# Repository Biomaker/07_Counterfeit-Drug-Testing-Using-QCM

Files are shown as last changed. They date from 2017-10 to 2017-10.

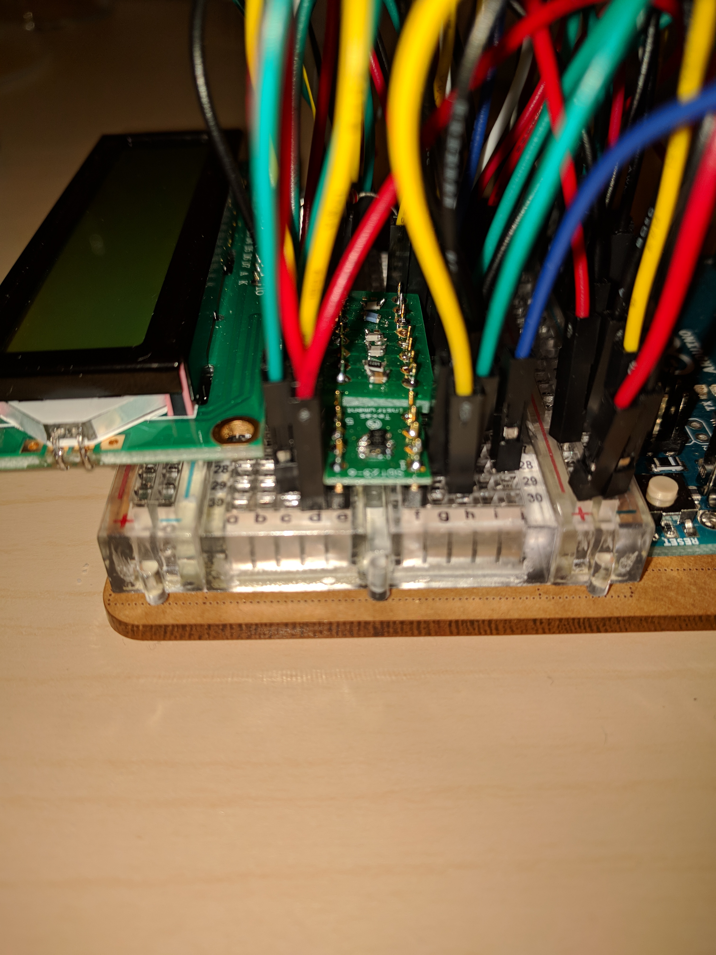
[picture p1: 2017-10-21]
Images/Surface_mount_components.jpg

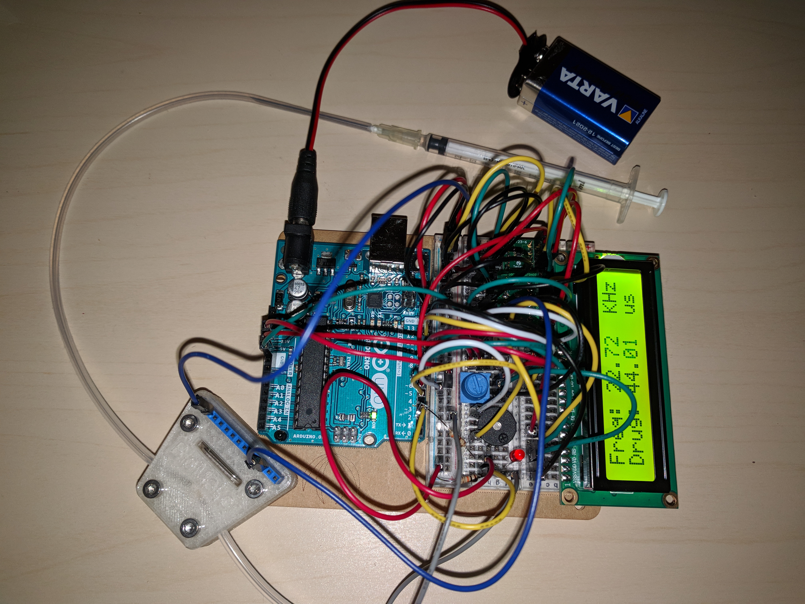
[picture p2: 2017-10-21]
Images/Complete_Setup.jpg

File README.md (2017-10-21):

## Synopsis

Malaria kills approximately a million people each year, and although efforts to produce and distribute effective drugs has increased, there is a growing problem with forged medications. Counterfeit antimalarial drugs cause an estimated 120,000 deaths in Africa per year , and detection methods are too expensive and/or too technically complex. Our objective is the development of a low cost counterfeit drug detection system that can be easily used in low-resource settings. The system builds on open-source quartz crystal microbalance technology to detect the presence of the active drug and its concentration. Easily contained in a handheld device that will give real-time feedback to the user, our method ensures the efficacy of global health measures by contributing to effective malaria elimination in at-risk communities.

## Software

The frequency output of the oscilator was connected to Arduino pin 5 as this is this pin must be used on the Arduino Uno when using the 16bit Timer/Counter1 of the ATmega chip as our code does.
The LCD was connected to pins 8,9,10,6,12,13 corresponding to RS,E,D4,D5,D6,D7 on our LCD display. Pin 6 was used instead of pin 11 as we anticipated using a buzzer output with the inbuilt "tone" function which can cause instabilities on pins 3 and 11. 

## Hardware

The included electrical schematics were used to set up the device. However the thermoresitor was excluded from our final implementation (couldn't get it to read in a reasonable valure).

The included CAD models were printed on an Ulitimaker 3. The inlet ports were connected to 2mm OD Silicone tubing whihc caused a press fit.

Rubber nitrile o-rings were used to support the QCM and form a seal.

M3 nuts and bolts were used to clamp the assembly together.

## Installation, Maintenance and Testing Guide

The frequency output of the oscilator was directed to pin 5 and written to the connected LCD.

Ideally this value would be compared to a stored value for the expected frequency response of the target analyte.

Pins 8-13 were used for readout to the LCD display

## License

A short snippet describing the license (MIT, Apache, etc.) you have chosen to use

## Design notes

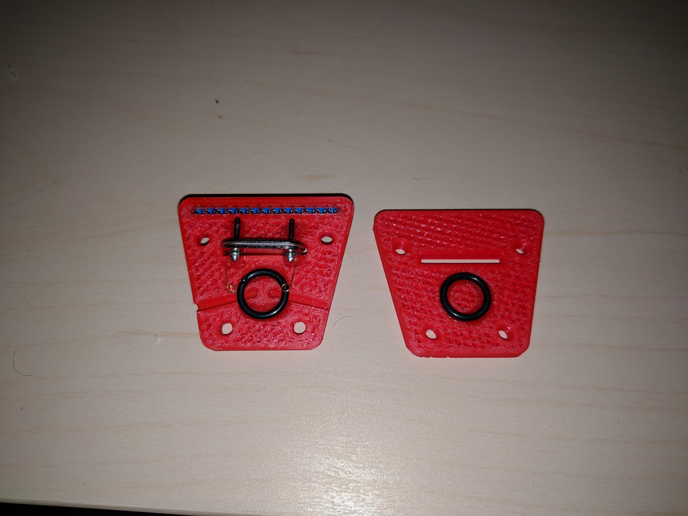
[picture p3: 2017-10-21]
Images/Internal_Channel.jpg

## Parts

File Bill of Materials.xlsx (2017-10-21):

Part | Minimum Order | Cost Per Order | Cost Per Unit | Required Units | Supplier | Part Number
3D printed | 750 | 30 | 0.8 | 1 | Ulitimaker
Socket Strip 2.54mm 14 Way 1 Row Straight PCB Socket Through Hole | 20 | 30.16 | 1.508 | 1 | RS | 252-406
Crystal Oscillator Driver | 10 | 7.81 | 0.781 | 1 | Texas Instruments | SN74LVC1GX04DBVT
Thick Film Resistors - SMD 1/8watt 1Kohms 1% 100ppm | 10 | 1.4 | 0.14 | 1 | RS | 679-0982
Thick Film Resistors - SMD 1/8watt 2.26Mohms 1% | 10 | 0.017 | 0.0017 | 1 | Vishay | CRCW08052M26FKEA
Multilayer Ceramic Capacitors MLCC - SMD/SMT 50volts 0.1uF X7R 10% | 10 | 0.45 | 0.045 | 1 | Kemet | C0805C104K5RACTU
Multilayer Ceramic Capacitors MLCC - SMD/SMT 50volts 100pF C0G 5% | 20 | 0.65 | 0.065 | 2 | Kemet | C0805C101J5GACTU
RESISTOR, 10KOHM, 0.125W | 10 | 0.65 | 0.065 | 1 | Onecall | 2352781
Thermistors - NTC 10Kohms 1% | 10 | 4.7 | 0.47 | 1 | OneCall | 2112901
Contact Clip Circuit Board Hardware - PCB | 20 | 2.18 | 0.218 | 2 | Harwin | S9101-46R
Quartz Crystal 10 Mhz Au electrode 13.9 x 6 mm | 10 | 114 | 11.4 | 1 | Open QCM | AT10-14-6-UP-10
Quartz Crystal holder | 10 | 17.5 | 1.75 | 1 | Open QCM | HC-48/U-EV
Nitrile Rubber O-Ring, 8.1mm Bore , 11.3mm O.D , -30 → +120°C | 50 | 2.92 | 0.1168 | 2 | RS | 0081-16 NBR
Syringe | 100 | 8.56 | 0.0856 | 1
Tubing | 50 | 36 | 0.72 | 20mm
M3 bolt + nut |  | 0.2516 | 0.7548 | 4
Total Cost per setup |  |  | 18.9209

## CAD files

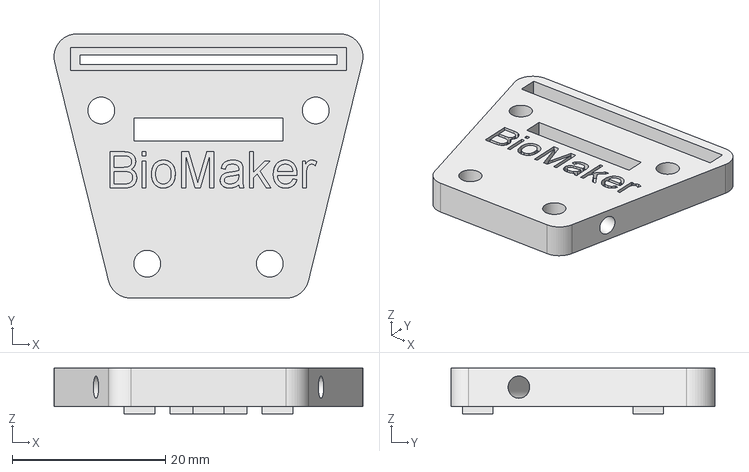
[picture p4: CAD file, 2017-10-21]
CAD Files/Top_v2.FCStd
40.3 x 34.5 x 6.00 mm

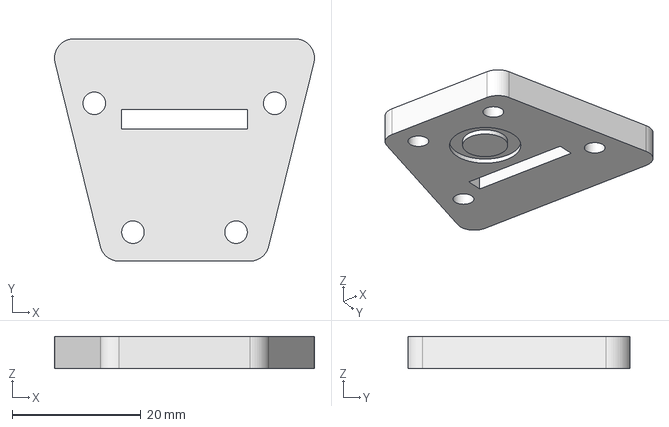
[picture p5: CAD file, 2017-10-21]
CAD Files/Base_v2.FCStd
40.3 x 34.5 x 5.00 mm

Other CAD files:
CAD Files/base_v2.stl
CAD Files/top_v2.stl

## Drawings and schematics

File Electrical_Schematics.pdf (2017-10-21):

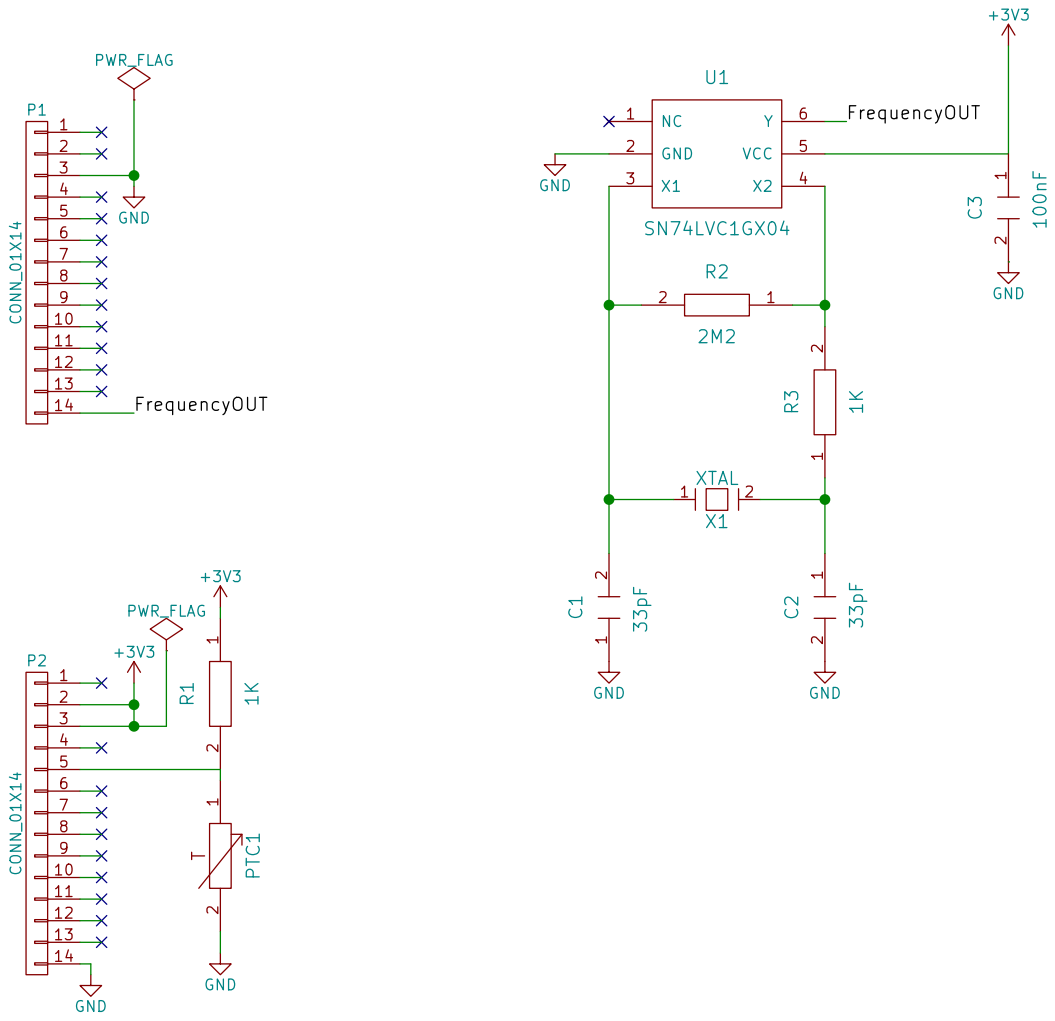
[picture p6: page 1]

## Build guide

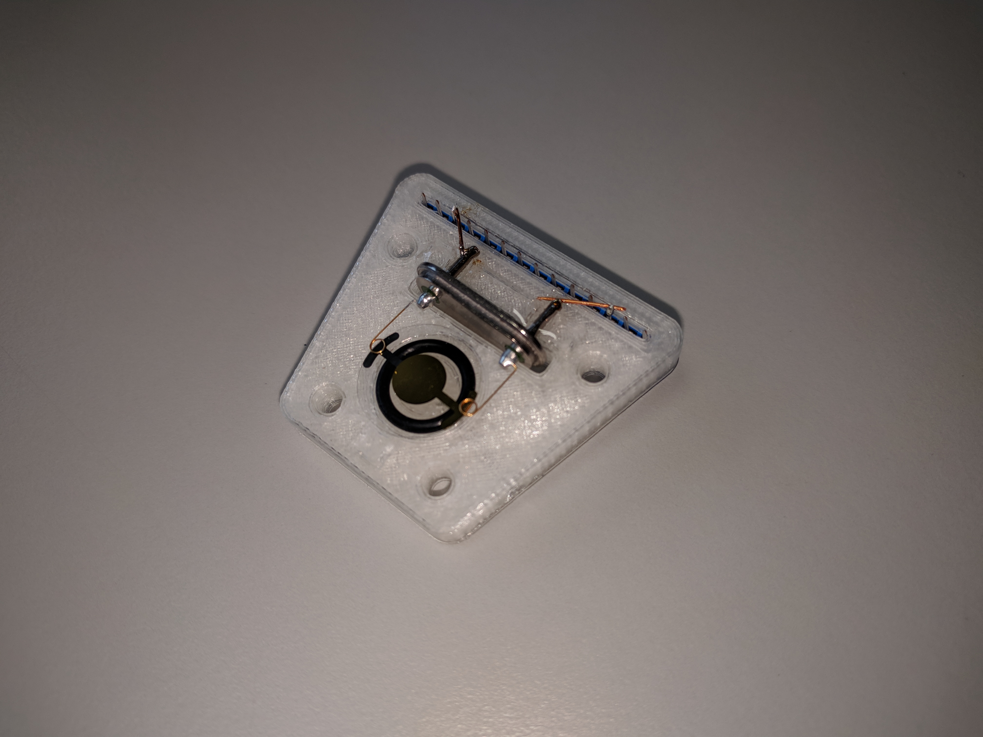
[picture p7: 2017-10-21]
Images/Internal_Crystal_Wiring.jpg

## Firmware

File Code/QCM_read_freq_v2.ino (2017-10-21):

/*  QCM Sensor With LCD - by Jason Brenker -Oct 2017 - adapted from Frequency Counter With LCD Display arduinoaleman - May 2015 

    Pin D5 of Arduino must be used for frequency input. The LCD uses pins 8 thru 13.
  
    Counter1 : 16 bits / used to count the frequency impules
    Counter2 : 8 bits / used to genarate a 1000ms or 100ms gate time for measurement
    
    Uses "bitClear(TIMSK0,TOIEO)" instead of "TIMSK0 &=~(1<<TOIE0)"
    Uses "bitSet(TIMSK0,TOIEO)"   instead of "TIMSK0 |=~(1<<TOIE0)"
   
 */

//Libraries for reading frequency and writing to display
#include <avr/interrupt.h>
#include <LiquidCrystal.h>

//Currently not used included for when a buzzer is included in design
#include "pitches.h"

//Sets pins for display, note pin 6 is used because when tone is implemented pin 11 could experience issues
LiquidCrystal lcd(8,9,10,6,12,13);

volatile unsigned long frequency=0;            
volatile boolean       measurement_ready;
volatile unsigned char overflow_counter;     // number of overflows within gate_time
volatile unsigned int  time_so_far;              // number of ISR calls
volatile unsigned int  gate_time;  

//This is currently not used, included to look for button press to activate measurment mode
// constants won't change. They're used here to set pin numbers:
const int buttonPin = 2;     // the number of the pushbutton pin
const int ledPin =  3;      // the number of the LED pin
// variables will change:
int buttonState = 0;         // variable for reading the pushbutton status

void measurement(int ms) {

    bitClear(TIMSK0,TOIE0);     // disable counter0 in order to disable millis() and delay()
                                   // this will prevent extra interrupts that disturb the measurement
    delayMicroseconds(66);      // wait for other interrupts to finish
    gate_time=ms;                  // usually 1000 (ms)

    // setup of counter 1 which will be used for counting the signal impulses
    TCCR1A=0;                  // reset timer/counter1 control register A
    TCCR1B=0;                  // reset timer/counter1 control register B
    TCCR2A=0;                  // reset timer/counter1 control register A
    TCCR2B=0;                  // reset timer/counter2 control register A
    
    // setup of counter2 which will be used to create an interrupt every millisecond (used for gate time)

    TCCR2B |= B00000101;        // set prescale factor of counter2 to 128 (16MHz/128 = 125000Hz)
                                   // by setting CS22=1, CS21=0, CS20=1

    bitSet(TCCR2A,WGM21) ;      // set counter2 to CTC mode
                                   // WGM22=0, WGM21=1, WGM20=0                   
    OCR2A = 124;                   // CTC divider will divide 125Kz by 125 
   
    measurement_ready=0;        // reset
    time_so_far=0;              // reset
    bitSet(GTCCR,PSRASY);       // reset the prescaler 
    TCNT1=0;                    // set frequency counter1 to 0
    TCNT2=0;                    // set gate time counter2 to 0
      
    bitSet(TIMSK2,OCIE2A);      // enable counter2 interrupts
    TCCR1B |= B00000111;        // set CS12, CS11 and CS10 to "1" which starts counting 
                                // on T1 pin (Arduino pin D5)
 }

ISR(TIMER2_COMPA_vect) {
   if (time_so_far >= gate_time) {  // end of gate time, measurement is ready
    TCCR1B &= B11111000;            // stop counter1 by setting CS12, CS11 and CS10 to "0"
    bitClear(TIMSK2,OCIE2A);        // disable counter2 interrupts
    bitSet(TIMSK0,TOIE0);           // enable Timer0 again // millis and delay
    measurement_ready=true;         // set global flag for end count period
// calculate now frequeny value 
    frequency=0x10000 * overflow_counter;  // mult #overflows by 65636 (0x10000)
    frequency += TCNT1;                    // add counter1 contents for final value
    overflow_counter=0;                    // reset overflow counter
  }
   else {
    time_so_far++;                         // count number of interrupt events
    if bitRead(TIFR1,TOV1)  {              // if Timer/Counter 1 overflow flag = "1" then ...
       overflow_counter++;                 // increase number of counter1 overflows
       bitSet(TIFR1,TOV1);                 // reset counter1 overflow flag
    }
  };
}

void setup() {
  // initialize the LED pin as an output:
  pinMode(ledPin, OUTPUT);
  // initialize the pushbutton pin as an input:
  pinMode(buttonPin, INPUT);
  pinMode(5,INPUT);
  lcd.begin(16, 2);            // defines a LCD with 16 columns and 2 rows
  lcd.clear();
  for (int row=0; row<=1; row++) {
     for (int column=0; column<=15; column++) {   // LDC test
      lcd.setCursor(column,row);
       lcd.print("*");
       delay(70);
      };
  }
  lcd.clear();
}

void loop() {
  float period;    
  float floatfrq;  
  int range;
  long frq;
  measurement(1000);       // 1000ms standard gate time
  while (measurement_ready==false);
  frq=frequency;
  floatfrq=frq;                    // type conversion (required!!)
  period=(1/floatfrq);                // period = 1/Frequenz - 

  if ((frq >= 0)&& (frq < 10)) {
    range=0;
      };                                             // Hertz
  if ((frq >= 10)&& (frq < 100)) {
    range=1;
    };   
  if ((frq >= 100)&& (frq < 1000)&& (buttonState == HIGH)) {
    range=7;
    };
  if ((frq >= 100)&& (frq < 1000)) {
    range=2;
    };
  if ((frq >= 1000)&& (frq < 10000)) {
    range=3; floatfrq=floatfrq/1000;
    };      // KHz
  if ((frq >= 10000)&& (frq < 100000)) {
    range=4; floatfrq=floatfrq/1000;
    };
  if ((frq >= 100000)&& (frq < 1000000)) {
    range=5; floatfrq=floatfrq/1000;
    };
  if (frq >= 1000000) {
    range=6; floatfrq=floatfrq/1000000;
    };          // MHz 
  
  lcd.setCursor(0, 0);                 
  lcd.print("Freq:           ");        
  lcd.setCursor(0, 1);                 
  lcd.print("Drug:          ");
   
  switch(range) {             
    case 0:                                          // 1Hz thru 10Hz
       lcd.setCursor(6, 0);   lcd.print(frq);
       lcd.setCursor(10,0);   lcd.print("Hz ");
       lcd.setCursor(5, 1);  lcd.print("Not Present");  
       digitalWrite(ledPin, LOW);
       break;
    case 1:   // 10Hz thru 100Hz
       period=period*1000;        // convert from seconds to ms       
       lcd.setCursor(6, 0);   lcd.print(frq);
       lcd.setCursor(13,0);   lcd.print("Hz ");    
       lcd.setCursor(5, 1);  lcd.print("Not Present");  
       digitalWrite(ledPin, LOW);
       break;
    case 2:    // 100Hz thru 1KHz
       period=period*1000; 
       lcd.setCursor(6, 0);   lcd.print(frq);
       lcd.setCursor(13,0);   lcd.print("Hz ");    
       lcd.setCursor(5, 1);  lcd.print("Not Present");
       digitalWrite(ledPin, LOW);             
       break;
    case 3:    // 1KHz thru 10KHz
       period=period*1000; 
       lcd.setCursor(6, 0);   lcd.print(floatfrq,3);
       lcd.setCursor(13,0);   lcd.print("KHz");    
       lcd.setCursor(5, 1);  lcd.print("DRUG FOUND!"); 
       digitalWrite(ledPin, HIGH);            
       break;
     case 4:   // 10KHz thru 100KHz
       period=period*1000*1000;                  
       lcd.setCursor(6, 0);   lcd.print(floatfrq,2);
       lcd.setCursor(13,0);   lcd.print("KHz");    
       lcd.setCursor(5, 1);  lcd.print("Not Present"); 
       digitalWrite(ledPin, LOW);       
       break;
      case 5:   // 100KHz thru 1MHz
       period=period*1000*1000;                      // convert from s to µ
       lcd.setCursor(6, 0);   lcd.print(floatfrq,1);
       lcd.setCursor(13,0);   lcd.print("KHz");    
       lcd.setCursor(5, 1);  lcd.print("Not Present"); 
       digitalWrite(ledPin, LOW);        
       break;
     case 6:   // above 1MHz
       period=period*1000*1000;
       lcd.setCursor(6, 0);   lcd.print(floatfrq,3);
       lcd.setCursor(13,0);   lcd.print("MHz");    
       lcd.setCursor(5, 1);  lcd.print("Not Present");  
       digitalWrite(ledPin, LOW);
       break;      
          
       break;       
  } 
}   

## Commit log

2017-10-21 Add files via upload
    Initial commit to test upload.
    [Base_v2.FCStd, Top_v2.FCStd, base_v2.stl, top_v2.stl]
2017-10-21 Add files via upload
    Supplier details and cost of components used.
    [Bill of Materials.xlsx]
2017-10-21 Add files via upload
    First attempt at reading the frequency output from the circuit. Adapted from the OpenQCM project by Inigo Ayestaran.
2017-10-21 Add files via upload
    Alternative code which runs on Arduino as stand alone device. Writes frequency to LCD, needs work to get lights, buzzer and button working to notify user when detection is taking place.
